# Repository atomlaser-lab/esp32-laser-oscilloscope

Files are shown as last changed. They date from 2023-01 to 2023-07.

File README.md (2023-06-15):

# ESP32 Remote Oscilloscope + MOGLabs DLC control

This project is a remote browser-based oscilloscope and controller intended for monitoring, toggling and adjusting the frequency lock on a MOGLabs Diode Laser Controller (DLC). An ESP32 development board interfaces with the DLC and hosts a dashboard webpage.

This README contains [Instructions](#instructions) for setting up and using the project as well as useful [Background information](#background). A list of [bugs and suggested improvements](#bugs-and-improvements) is at the end. The project was developed and tested using the PlatformIO Extension in VSCode, with a model 502 DLC. It requires an ESP32-DevkitC development board (see [specs, board comparison & resources](https://www.espressif.com/en/products/devkits/esp32-devkitc)), and should work with either WROVER or WROOM versions. It was tested with the ESP32-DevKitCVE V4 board, which has a WROVER module.

## License
[GPLv3](LICENSE)

## Repository structure
Branches: currently just `esp`. Branches for other microcontrollers might be useful in future.

PlatformIO:
- `src/main.cpp`: ESP32 code.
- `data/`: files stored on the ESP32 flash memory. Contains the webpage + `config.json`.
- `platformio.ini`: PlatformIO project config.

Hardware:
- `board-design/`: TODO
- `enclosure/`: FreeCAD files for the 3D-printable housing.

Other:
- `.vscode`: recommended extensions
- `assets/`: images for this README.

## Instructions
[Software config](#program-configuration-and-upload) - [Hardware](#hardware-connections-and-settings) - [Browser interface](#interface)

### Program configuration and upload
This section assumes you are using the PlatformIO extension in VSCode.

Specify project options by editing `config.json` (in `/data`). If connecting to an existing WiFi network (the default option), you must specify its `ssid` (network name) and `password`. If instead `host` is set to `true`, the ESP will host its own network (intended for testing purposes) with credentials `host_ssid` and `host_password`. `host_password` must contain at least 8 characters; otherwise hosting will fail. Note that the ESP32 only supports 2.4GHz WiFi (not 5G).

Other parameters are optional, with defaults and descriptions as shown below in **Example 2**.

**Example 1: minimal WiFi connection**
```
{
  "ssid": "MyWiFiNetwork",
  "password": "verysecurepassword",
}
```

**Example 2: all options**
```
{
  "name": "TestName",
  "host": false,
  "ssid": "MyWiFiNetwork",
  "password": "verysecurepassword",
  "host_ssid": "ESP32_Laser_Lock",
  "host_password": "laserlock",
  "host_channel": 1,
  "default_duration": 60,
  "default_resolution": 2,
  "default_ip": "192.168.1.1"
}
```

| Parameter | Description |
| --- | --- |
| `name` | Display name for the device |
| `host_channel` | If hosting, the WiFi channel used. |
| `default_duration` | Default length of a measurement packet (millisec), adopted on board startup. |
| `default_resolution` | Default time (ms) between consecutive samples in a measurement packet, adopted on startup. |
| `default_ip` | If available, the local IP address the ESP32 will adopt. Applies to both hosted and external networks. |

To **upload the project to the board**:
1. Connect the board to your computer via a cable.
2. Upload the filesystem to the board:
    - '*Build filesystem Image*' (in PlatformIO menu)
    - **Ensure all serial monitor connections with the board are closed**. PlatformIO does not do this automatically when uploading the filesystem (though it *does* when uploading the code in step 4)
    - '*Upload filesystem Image*' (in same menu)
3. '*Build*' (PlatformIO menu, or tick symbol in status bar)
4. '*Upload*' (PlatformIO menu, or rightwards arrow in status bar)

The program will restart each time the ESP is plugged in, code/filesystem is re-uploaded, or the RST button is pressed.

Open the serial monitor to see the board's local IP. You may need to reset the program (RST button) while the monitor is open for the message to display. If `default_ip` is specified (and was successfully adopted), you can skip this step.

Connecting to the board's IP in a browser (e.g. `http://192.168.1.1`) while on the same network will open the [Interface](#interface).

### Hardware
This section assumes you already have a laser-locking setup using the MOGLabs DLC. For information about laser locking and the DLC, see [Background](#background).

#### Overview
The MOGLabs DLC contains fast, robust analog control circuitry for locking the laser frequency. The point of this project is to allow the lock to be acquired via microcontroller control of the DLC, while leaving the DLC to handle the actual locking process.

The project currently has three inputs and three outputs. The photodiode , error and trigger (digital) signals from the DLC are input to the board and transmitted to the remote user interface. The board outputs two digital (TTL) control signals to enable/disable the FAST and SLOW lock, and an analogue signal (via external DAC) to adjust the laser's frequency offset. More detailed reasoning behind the electronic design is explained in [Hardware design](#hardware-design).

The next section contains some guidance for putting together the PCB. The ESP32 board can be soldered to the PCB directly for the smallest possible footprint, but it is much more flexible to attach it via additional male and female headers. The external frequency offset voltages used in this project also require soldering an additional resistor into the DLC (see [Connecting to the Diode Laser Controller](#connecting-to-the-diode-laser-controller)). 

Part numbers and quantities for **two** PCBs are specified in `board-design/moglabs-remote-locking-board.txt` for the DigiKey electronics distributor, which can be imported directly into a DigiKey cart. This list is missing capacitors C6 and C7 (see table below). Auxiliary parts (headers + DLC resistor) are similarly specified in `board-design/auxiliary-parts.txt`. An optional 3D-printable housing for the project can be found under `enclosure/`. 

Electronic design was done in KiCAD 6, and the (optional) enclosure was generated with FreeCAD 0.20.2.

#### Printed Circuit Board
Relevant files are in `/board-design`. Gerber files for manufacturing the PCB can be found in `generated.zip`, and PCB circuit and layout schematics (`.pdf`) are under `plots/`.

```
board-design/
|-- generated.zip
|-- plots/
  |-- moglabs-remote-locking-board.pdf
  |-- moglabs-remote-locking-board.pcb
|-- moglabs-remote-locking-board.txt
|-- auxiliary-parts.txt
|-- ...
```

This section briefly describes the circuit, shown below. For more details, see `board-design/README.md`.

Left: input for the error signal ('Lock'), photodiode signal ('PD') and trigger. A 1.5V offset is added to the (bipolar) error signal to make it positive, and both Lock and PD voltages are clipped to remain within the board's 0-3.3V pin range. The DLC trigger is +5V, which is divided down accordingly.

Bottom left: power regulator to introduce +5V and -5V VDD and VSS rails from the board's 5V power pin.

Right: analog frequency-offset output signal (J6) controlled by an external DAC (U4) and dual opamp (U3). The DAC output is divided down considerably, as a 1V adjustment to PZT MOD corresponds with about a third of the piezo's (i.e. frequency) range. A variable resistor gives additional control over the output voltage range (this will need to be tuned to observe an output signal).

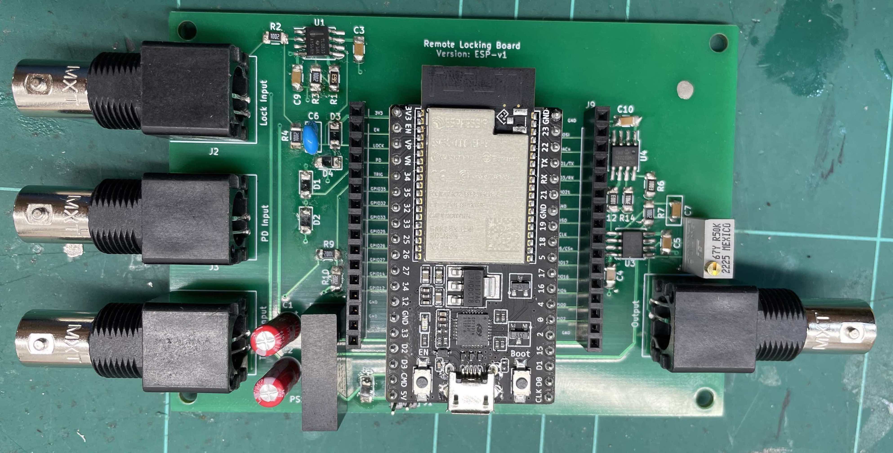
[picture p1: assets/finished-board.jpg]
Soldered board


The required parts for **one** PCB are in the tabe below. For specific part numbers, see the DigiKey text files specified above. Note that the capacitor numbering in the schamatic skips C8.

Terminology:
- 8-SOIC is a component shell size/type (comonly opamps, dacs)
- DAC: digital-to-analogue converter
- SPI: Serial Peripheral Interface
- SMD: Surface-mounted device
- 1206: component size

| Requirement / Part description | PCB Locations | Total Qty | Notes |
| --- | --- | --- | --- |
| IC 8SOIC 12-Bit single-output DAC with SPI and internal voltage reference (2.048V/4.096V) | U4 | 1 | code assumes [MCP4821](https://www.microchip.com/en-us/product/MCP4821) |
| IC 8SOIC JFET opamp 1-circuit | U1 | 1 | |
| IC dual (2-circuit) opamp GP 8SOIC | U3 | 1 | |
| ESP32 DevKitC VE (WROVER/WROOM) | U2 | 1 | |
| 16-position 2.54mm female row header | J5, J9 | 2 | |
| 2-pos 2.54mm male header | J1 | 1 | |
| 50 kΩ potentiometer 0.5W | RV1 | 1 | |
| DC DC converter dual 5V 1W | PS1 | 1 | |
| BNC socket | J2, J3, J4, J6 | 4 | |
| 40V 1A Schottky diode (SMD 1206) | D1,D2,D3,D4,D5 | 5 | |
| 100 nanofarad 50V ceramic capacitor (SMD 1206) | C3, C4, C5, C9, C10 | 5 | |
| Polarised through-hole capacitor 4.7 uF 25V | C1, C2 | 2 | |
| 10 nF through-hole capacitor | C6 | 1 | Not on DigiKey list |
| 100 nF through-hole capacitor | C7 | 1 | Not on DigiKey list |
| 10 kΩ 0.5W resistor (SMD 1206) | R2, R3, R4, R7, R9 | 5 | |
| 20 kΩ 0.5W resistor (SMD 1206) | R10 | 1 | |
| 100 kΩ 0.5W resistor (SMD 1206) | R6, R12 | 2 | |
| 3.9 kΩ 0.25W (SMD 1206) | R14 | 1 | |
| 56 kΩ 0.25W resistor (SMD 1206) | R1 | 1 | |

Optional headers for mounting the ESP32 devkit on the PCB:

| Description | PCB Locations | Total Qty | Notes |
| --- | --- | --- | --- |
| 19-position 2.54mm female header | J7 & J8 (not marked) | 2 |  |
| 19-position male header for ESP32 | On ESP32 | 2 | Likely included with ESP32 devkit |

#### Tests
- TODO

#### Connecting to the Diode laser controller
Take care when connecting to the DLC, particularly to avoid shorting the digital control pins. Ensure the internal DIP switch settings of the DLC are set appropriately (e.g. as in [Moglabs Diode Laser Controller](#moglabs-diode-laser-controller)). For reference, at the end of this section are the DLC panels (from the [DLC manual](https://www.moglabs.com/products/laser-electronics/diode-laser-controller)) and the location of the HD12 header.

##### **POWER**
The board can be powered via the micro-USB connector (5-12V) or the PCB's J1 two-pin header (5V).

The DLC has an IEC output (rear panel, second from the left), which is a direct connection to the DLC's input power (after the mains filter) and can be used to power the ESP32 using an IEC cable and 12V power adapter. This is convenient and ensures the ESP32 shares the same ground as the DLC.

Safe input voltages for the board's pins are 0-3.3V, and is it **not** tolerant of voltages outside this range. Be careful to keep the DLC and ESP32 ground voltages compatible.

##### **SLOW and FAST**
Digital control of the DLC is via the internal HD12 header, which is located as shown below. **Do not** confuse it with the similar-looking header nearby. The ESP's digital pin voltages are compatible with the HD12 header and can be connected directly as per the table below.

| Board pin | HD12 pin(s) |
| --- | --- |
| GPIO14 | 3 |
| GPIO4 | 5 |
| GND | 4, 6 |

Ensure that the sweep range is set appropriately, and that the front-panel LOCK and FAST switches are **off** so that these can be enabled remotely.

##### **TRIGGER**
The MOGLabs DLC trigger signal output (TRIG on rear panel) fires a +5V rising edge (i.e. 0V to 5V) at the trigger point of the sweep, i.e. the *centre* if using the DLC's default (internal) sweep. This can be safely connected to the appropriate BNC input on the PCB.

##### **INPUT SIGNALS**
Set the CHAN A and CHAN B selector dials to (photodiode) Input and (feedback) Error respectively; note that both channels can output the photodiode, but only CHANNEL B can output the error signal. Connect these to their respective PCB inputs.

The photodiode input offset and error signal offset can be adjusted respectively using the INPUT and ERROR OFFSET dials on the DLC's front panel. The photodiode should be in the range 0-3.3V, and the error centred for locking (i.e. about zero).

##### **FREQUENCY CONTROL**
Test the frequency control output (J6) before connecting, to ensure it is within the range +/- 0.2V. Before connecting, a 5kΩ resistor must be added at location R113 on the DLC's circuit board to allow adding an external frequency voltage offset.

| Description | **DLC** location | Total Qty |
| --- | --- | --- | --- |
| 5kΩ size 0603 SMD resistor  | R113 | 1 |

Once this is added, connect J6 via BNC to the DLC's SWEEP/PZT MOD input.

##### Reference images

**Location of HD12 Header**
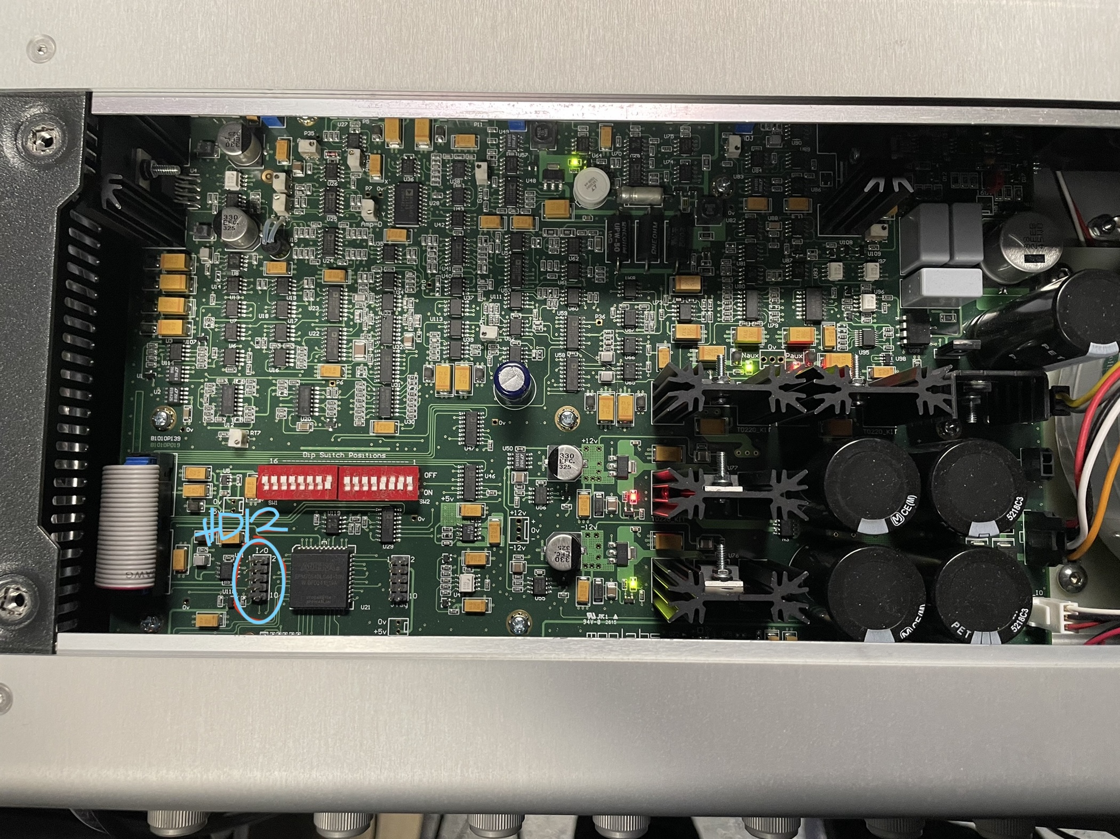
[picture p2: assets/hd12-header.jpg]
HD12 header location


**Front DLC panel**
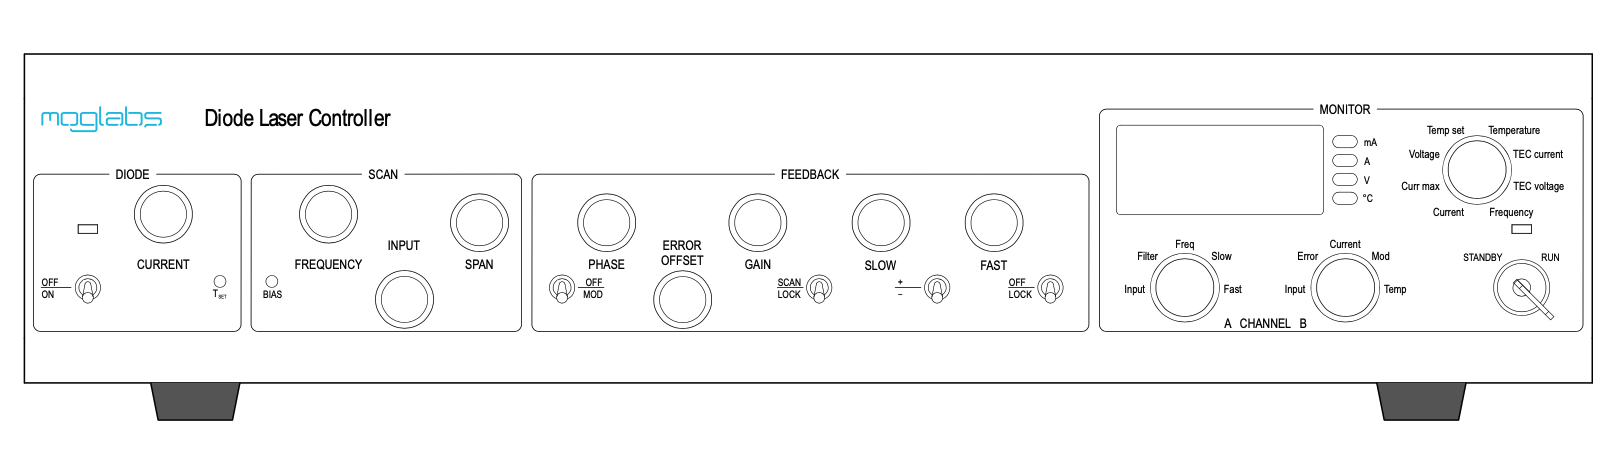
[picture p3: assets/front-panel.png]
DLC502 front panel


**Rear DLC panel**
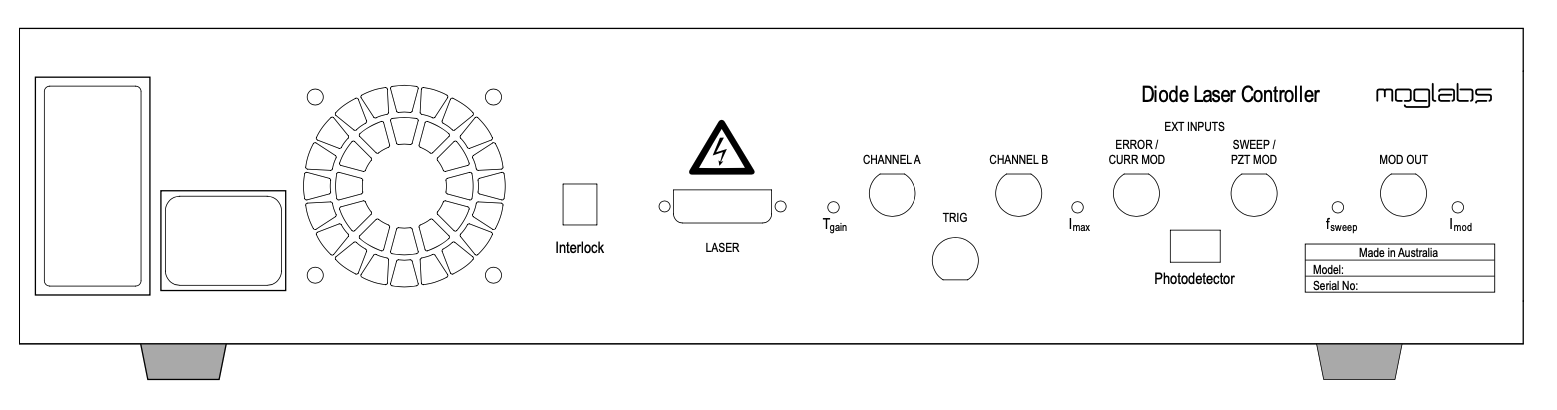
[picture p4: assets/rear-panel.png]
DLC502 rear panel


### Interface
Connecting to the board's IP in a browser should display the page below. If you didn't set the IP in `config.json`, you can list the devices on the local network using `arp -a` in a terminal, or check the IP by restarting the ESP32 while connected to the serial monitor.

Only one user is allowed to connect at a time, to prevent conflicting commands.

Controls for the DLC, the ESP32, and the browser display are split into three separate panels.

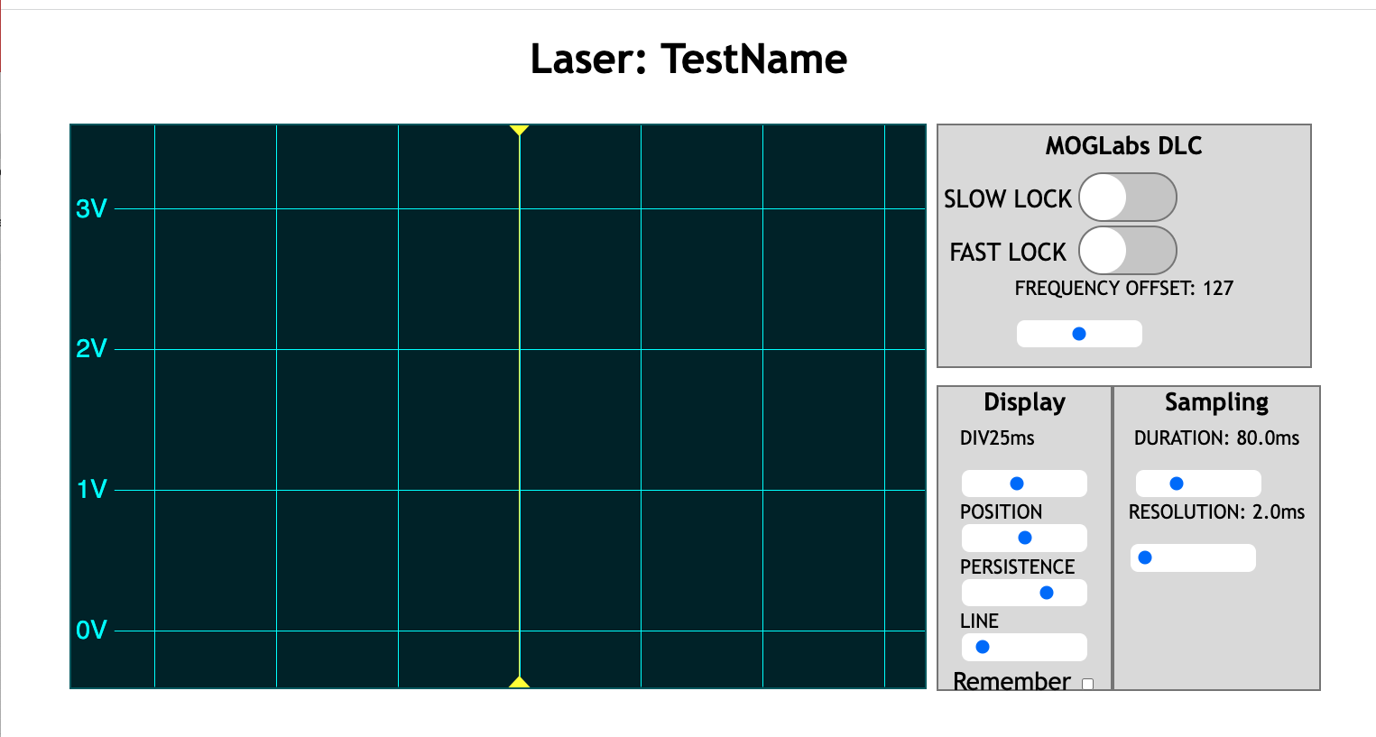
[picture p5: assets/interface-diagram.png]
Interface diagram


#### DLC Control
The top panel has switches for toggling the SLOW and FAST lock. These switches are subject to a cooldown, and will also only change appearance once the ESP has confirmed the command was successful.

The 'Frequency Offset' slider controls the external voltage to the piezo. The displayed number is arbitrary.

#### Sampling settings
Signal measurements are sent from the board to the browser in groups. The RESOLUTION and DURATION sliders respectively control the time between individual measurements and the size of each group sent to the browser.

#### Display settings
These affect how the signal is displayed in the browser. Check 'Remember' to remember these settings.

| Slider| Function |
| --- | --- |
| DIV | Time period represented by each horizontal interval on the display. (i.e. horizontal scaling) |
| POSITION | Horizontal position of the trigger point in the signal, marked by the yellow indicator. |
| PERSISTENCE | How quickly previous trigger signals fade from the screen. |
| LINE | The line thickness. |

## Background
This section explains useful background on laser operation and the MOGLabs DLC, as well as summarising relevant details about the ESP32 and giving an overview of how the program works.

### Lasers (motivation and operation)
In various applications we would like to 'lock' the frequency of a laser to a specific atomic transition frequency, either because these are physically constant and known to high precision or because we are working with that particular transition.

The output power and frequency of an external-cavity diode laser (ECDL) (TODO: useful reference here) are controlled primarily (though to differing extents) by three factors:

1. Current injected to the diode
2. Temperature
3. Cavity length (controlled by piezo voltage).

An ECDL internally permits light to (co)exist at a discrete set of frequencies ('modes') determined by the length of the cavity. This light bounces back and forth through a 'gain medium', which repeatedly amplifies it (up to the limit of power provided by the injection current). On each trip, a small amount exits the cavity. The diagram below is an example of frequency-dependent gain (black) affecting different modes (red) (image credit: [this stackexchange answer](https://physics.stackexchange.com/questions/355223/laser-gain-curve) under the [CC BY-SA 4.0 license](https://creativecommons.org/licenses/by-sa/4.0/)).

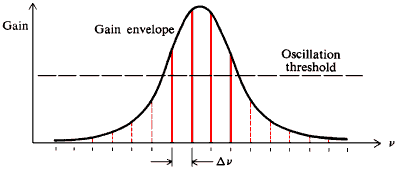
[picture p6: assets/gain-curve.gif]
Gain curve diagram


At a given temperature and injection current, the gain medium amplifies different frequencies by different amounts, known as a gain curve. When 'lasing' (i.e. sufficiently high current), the most strongly-amplified of the allowed modes will quickly dominate, producing a single-frequency output (provided this amplification is enough to overcome losses).

Even with constant current, temperature and cavity length, the laser frequency tends to drift, which is mitigated using feedback. However, if two modes have similar amplification, the dominant one can switch erratically ('mode hopping') with a corresponding distinct jump in frequency. These jumps typically can't be remedied by feedback, requiring the laser to be re-locked. The aim of this project is to allow this re-locking to be performed remotely.

### Frequency locking (Saturated absorption spectroscopy)
To produce an error signal, we make use of the fact that an atom will only absorb light that is near a transition, roughly within a linewidth (i.e. ~inversely proportional to the lifetime of the corresponding state). Linewidths vary between kHz and GHz.

[ TODO: diagram of vapour cell with counterpropagating beams ]

Suppose a laser passes through a gas. The *apparent* frequency of the laser depends on the velocity of an atom (the Doppler effect). Since the atoms have a range of velocities, the laser will be absorbed in rough proportion to the number of atoms at the corresponding velocity, so the range of absorbed frequencies is 'Doppler-broadened' and the output intensity varies on the order of GHz.

If we reflect the laser back through the cell, it will now excite (i.e. be absorbed by) atoms of the *opposite* velocity, reducing the intensity again. This will not occur, however, if these atoms were *already* excited by the forward beam, i.e. if the beam is exactly on resonance with the zero-velocty atoms. So, we get a small dip in absorption when at the transition frequency.

[ TODO: diagram of doppler-broadened peak and saturation dip]

[ TODO: diagram of Rb85 absorption spectrum and error signal, e.g. DLC manual Fig. 1.3]

We can use the absorption dip as a reference point via either *AC* or *DC* locking. In both cases, we first produce an *error signal* whose voltage indicates the sign and size of any frequency drift, being zero at the reference point. Any error is then corrected via a feedback signal to the laser.

DC locking uses the absorption signal itself (as measured by the photodiode) as the error signal, by applying a voltage offset so that the signal passes zero on the side of the absorption peak. However, this easily becomes unlocked as the laser power drifts relative to the reference voltage.

AC is more reliable and allows you to lock exactly to the peak of a signal. This is done by rapidly shifting the signal from side to side, by deliberately modulating (dithering, i.e. rapidly oscillating) either the laser frequency (via the injection current) or the atomic resonance frequency (via a magnetic field). The MOGLabs DLC supports both methods, but in this case we used the former. Passing the modulated signal through a lock-in amplifier yields the derivative of the absorption spectrum, which passes through zero at the centre of the peak and hence serves as an error signal.

### MOGLabs Diode Laser Controller
This section is a reference for how the DLC works, convering information relevant to the design and understanding of the project. It summarises parts of the MOGLabs DLC manual (description and manual [here](https://www.moglabs.com/products/laser-electronics/diode-laser-controller)) and my own experience. The DLC's settings are mostly controlled via internal DIP switches (small, manual switches). Below is a reference; selections used in this project are in bold, and a brief explanation is on the right. The rest of this section will hopefully make clear what these DIPs do. 

| DIP Switch | Off | On | Relevance |
| --- | --- | --- | --- |
|1 | **DISC fixed** | DISC ON| Our laser doesn't have DISC |
|2 |STACK fixed| **STACK ON**| Enables control of the piezo |
|3 |Current dither OFF| **Current dither ON** | Enables *laser current* modulation when OFF/MOD is enabled |
|4 |Current bias OFF| **Current bias ON**| Enables BIAS, to avoid mode hopping|
|5 |**Internal error**| External error| We use the DLC's generated error signal
|6 |**External current mod OFF**| External current mod ON| Leave the DLC to do its thing
|7 |**AC lock**| DC lock| AC locking is more reliable
|8 |**Single photodiode**| Dual photodiode| Measuring direct intensity or the difference of two intensities, using the MOGLabs photodiode.
|9 |**Sweep internal**| Sweep external| Internal sweep works well, and SWEEP/PZT mod is needed for electronically adjusting the frequency offset
|10| STACK feedback –| STACK feedback +| Depends on your setup
|11| STACK sweep +| STACK sweep –| Depends on your setup
|12| **AC current feedback** | DC current feedback| FAST feedback should usually be AC no matter what
|13| **STACK internal**| STACK external| We want the DLC to control STACK, not us.
|14| DISC internal| DISC external| Irrelevant if no DISC.
|15| Default| External slow error| See manual
| 16 | See manual.

The DLC controls all three of the ECDL's piezo voltage (cavity length), temperature and injection current. The voltage applied to the piezo is known as the STACK (some lasers have a second piezo, *DISC*, which can also be controlled - I ignore that here.). At any given time, the DLC is either SCANning or LOCKing the laser frequency.

The voltage supplied to STACK ranges from 0-120V. When scanning, this voltage is adjusted according to the DLC's *sweep signal*, which has a range of 0-2.5V. The width of the scan (corresponding with full 0-2.5V range) is controlled by the SPAN dial and cannot be controlled externally. The DLC's trigger fires when the sweep signal crosses 1.25V; when locking is activated, the laser is first moved to this point before locking to the nearest zero-crossing of the error signal. Offsets to the input signal and error signal are adjusted using the INPUT OFFSET and ERROR OFFSET dials, respectively.

The DLC can either generate its own internal sweep signal, or use an *external* signal input to SWEEP/PZT MOD. The direction (polarity) of the internal sweep can be chosen using DIP switch 11, and its frequency can be varied between 4Hz-70Hz using the *fsweep* front panel trimpot. Diagrams of the internal sweep and corresponding trigger output are provided in the manual (Fig. 1.2). The sweep sawtooth is illustrative only; the DLC doesn't produce a sawtooth with perfectly vertical edges - they actually have a slight slope, to prevent the piezo from snapping back into place too forcefully (which creates a rattling sound). If this still happens, you may need to reduce the sweep frequency (fsweep trimpot) or SPAN.

The piezo offset (i.e. laser frequency) at the lock point is determined by the FREQUENCY dial. In particular, it is *not* affected by the use of an external sweep signal, which is only useful for controlling the speed, shape and (potentially asymmetric) width of the frequency path up to the maximum width set by SPAN. To limit mode-hopping while scanning, the diode current can be 'biased' to adjust itself linearly with the sweep voltage; this is enabled using DIP switch 4, with the direction and extent of adjustment controlled by the BIAS front trimpot.

#### Locking
The DLC provides feedback to the laser via:

1. The (relatively SLOW) piezo - for larger, slower drifts
2. The (comparably FAST) injection current - for small, rapid frequency fluctuations.

Each feedback is enabled by the corresponding switch (or digital control), and the direction can be reversed using DIP switch 10. The choice of AC or DC locking is controlled by DIP 7. The DLC provides an optional 250kHz modulation (switch OFF/MOD on front panel), either as an output (for e.g. dithering the atomic resonance) or directly to the laser current (see DIP switches); this is intended to aid AC locking. In either case, the amplification of the error, slow feedback and fast feedback can each be adjusted from 0-40dB via the GAIN, SLOW and FAST dials respectively. In the AC case, the phase of the lock-in amplifier (PHASE) may also need adjusting. Phase can be used to switch the sign of the SLOW feedback; to switch the sign of the FAST feedback, use the +/- switch. Note that the the MOGLabs photodetector outputs 30mV/microWatt.

Depending on which DIP switches are active, the SWEEP/PZT MOD input (rear panel) allows replacement of either the sweep signal (DIP 9), error signal (DIP 15) or direct piezo control voltage ('STACK') (DIP 13) with an external signal. However, the **only option** to externally adjust the lock frequency while making use of the DLC's (fast, robust, analogue) inbuilt control circuitry is to instead add a resistor (~5kΩ, size 0603) at location R113 (see the DLC manual), while leaving the aforementioned DIP switches OFF. This *adds* the SWEEP/PZT MOD input voltage to the existing laser piezo signal (STACK) under all circumstances (after a 48x scaleup).

Digital control of the DLC is via its internal HD12 control header, with the following pins:

| Pin | Signal |
| --- | --- |
|1 | Laser ON (low: off) |
|3 | Slow Lock (low: sweep) |
| 5 | Fast Lock |
| 7 | Hold |
| 9 | +5V |

Pins 2,4,6,8,10 are ground. 

These control pins are OR-ed with the front panel switches, so digital locking control only applies if the SCAN/LOCK switch is set to SCAN, and (for fast lock) the OFF/LOCK switch to OFF.

### ESP32
The ESP32 is a system-on-chip (SoC) with built-in WiFi, with input-output access via a *module*. For ease of use, this is often mounted on a *development board*, which provides easy pin access and various other useful components (e.g. ADC, voltage regulation). The same board 'form factor' (shape and pin arrangement) can be paired with different module versions; this project requires a ESP32-DevKitCVE V4 board, either with the ESP32-WROOM or ESP32-WROVER module.

An excellent introduction to the ESP32 can be found at [Last Minute Engineers (LME)](https://lastminuteengineers.com/getting-started-with-esp32/). This includes tutorials on ESP web servers and GPIO interrupts, both of which are used in this project. However, their tutorial uses (1) an older and slightly different board and (2) the Arduino IDE, while this project was developed using the PlatformIO IDE for VSCode (including the instructions in this README). 

An excellent video tutorial for PlatformIO+VSCode can be found [here](https://www.youtube.com/watch?v=JmvMvIphMnY). The project's source code uses the ESP32 Arduino framework ([documentation here](https://espressif-docs.readthedocs-hosted.com/projects/arduino-esp32/en/latest/index.html)). 

For the DevKitC-V4, a look at the [Getting Started Guide](https://docs.espressif.com/projects/esp-idf/en/v4.4.5/esp32/hw-reference/esp32/get-started-devkitc.html). Detailed specs can be found in the [official ESP32 datasheet](https://www.espressif.com/sites/default/files/documentation/esp32_datasheet_en.pdf). Below is the pin reference from the Getting Started Guide (note GPIO stands for General Purpose Input Output):

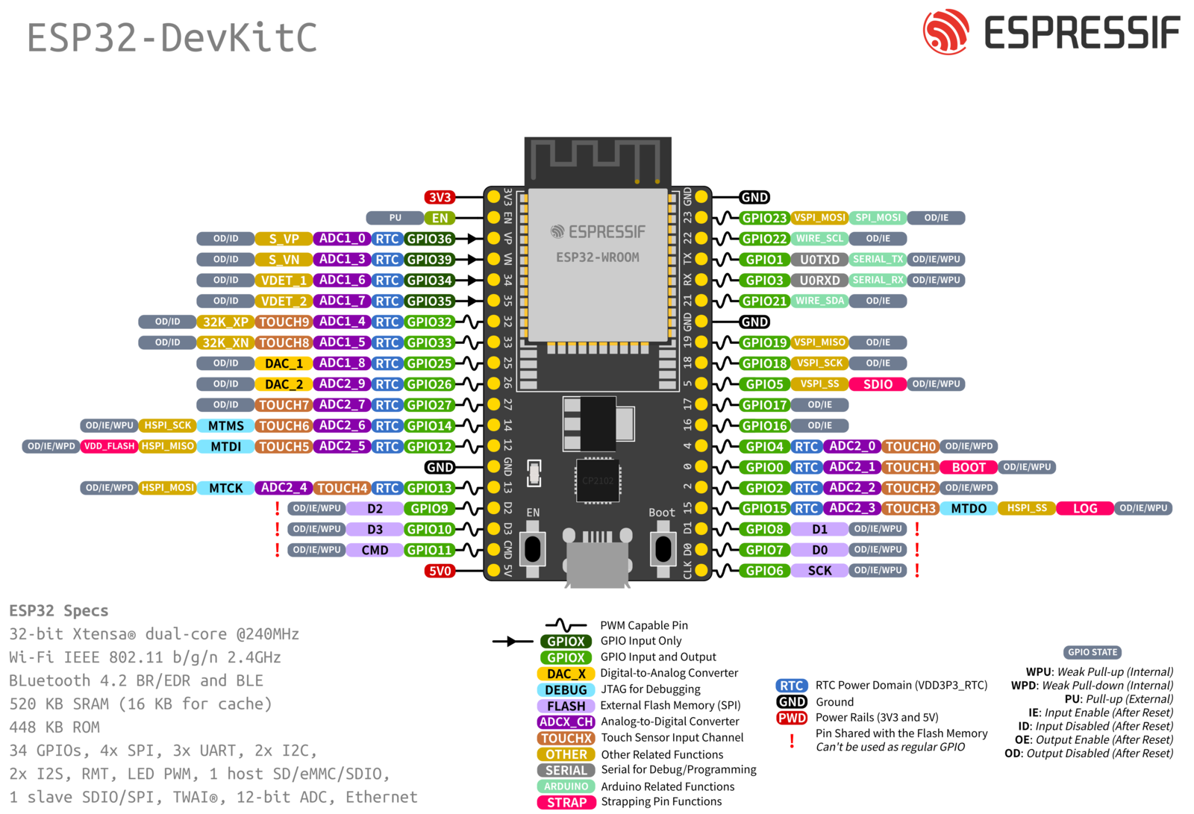
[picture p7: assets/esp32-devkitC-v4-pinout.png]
ESP32 pin reference


Note that not all pins are safe to use; this is discussed more in [Hardware design](#hardware-design).

The ESP32 has two 12-bit analog-to-digital converters (ADCs), which together can read analogue inputs from fifteen pins; however, ADC2 cannot be used while WiFi is in use, and so the analog input pins for this project have been chosen from those available to ADC1. Note that this issue prevents use of the (similar but less powerful) ESP8266 for this project, as it has only one ADC (which is WiFi-blocked).

ESP32 also has [a digital-to-analog converter](https://docs.espressif.com/projects/esp-idf/en/latest/esp32/api-reference/peripherals/dac.html) (DAC); however, this was not sufficient for this project.

The ESP32 only operates on 2.4GHz WiFi band (not 5.8GHz). The longevity commitment for the original ESP32 module is until [Jan 1, 2028](https://www.espressif.com/en/products/longevity-commitment)

### Hardware design
This section explains some details affecting the electronic design of the PCB.

The pins on the ESP32-DevKitC-V4 are (officially) only tolerant of 0-3.3V voltages, requiring appropriate input clipping for protection. The DLC's trigger is a 0-5V square signal, 

The previous section noted that only one of the ESP32's two ADCs can be used concurrently with WiFi. More importantly, WiFi use causes periodic spikes in power draw, which adds enough noise to the DAC output to prevent successful laser locking. Neither the board's inbuilt power regulator, nor additional bypass capacitors on the frequency-control output signal, are enough to avoid the issue. Therefore, we use an external MCP4821 DAC controlled via Serial Peripheral Interface (SPI). This also has a 12-bit resolution, higher than the inbuilt 8-bit DAC. The impedance of the SWEEP/PZT MOD input on the DLC is 5kΩ.

#### Pin choice
Can't use TX & RX pins, as they're used when flashing the board (even via USB). Pins which affect boot mode (0, 2, 12, 15) have been left alone. WROVER reserves GPIO 16/17 for internal use (controlling the SPI PSRAM). Inbuilt DAC (GPIO25/26) and the remaining ADC1 pins (GPIO33,32,35) have also been left available.

See Last Minute Engineers and [the boot mode docs](https://docs.espressif.com/projects/esptool/en/latest/esp32/advanced-topics/boot-mode-selection.html).

#### External DAC

This project uses the MCP4821 DAC to produce the frequency-adjustment signal, controlled from the ESP32 via serial peripheral interface (SPI).

The ESP32 has two SPI buses available for general use: SPI2 (HSPI) and SPI3 (VSPI). 'H' and 'V' don't signify anything. Any pins can be set as the corresponding interface pins; the defaults are indicated in the pinout diagram, but in this project non-default pins are used.

SPI communication with the MCP4821 is explained in its datasheet. Briefly: chip-select is driven LOW to initiate each data transfer, then 16 bits are transferred: four config bits followed by 12 value bits. The value bits are stored in the DAC's input register, and transferred to the output (Vout) when LDACn is pulled low. The current software keeps LDACn permanently low, so that the input value is transferred immediately to output.

### Software design
This section gives a general overview as well as some relevant details of the code. Many more comments are scattered throughout the source.

On startup, the ESP32 reads from `config.json`, sets up WiFi as a host or station accordingly, and begins a webserver (run asynchronously in the background) to serve the static webpage interface. Only one user is allowed to connect at a time, to prevent conflicting commands.

Since the MOGLabs DLC fires its trigger in the *middle* of each sweep, the simplest way to capture the entire sweep is to continually measure the input signals. The signal is sampled in 'packets', with a certain interval between each sample (~0.1-10ms), and a specified packet duration (~30ms-1s) before it is sent to the web client and a new packet begun. For simplicity, each 12-bit ADC measurement is reduced to a single byte (8-bit). Triggers fire an interrupt which records the time of the trigger in microseconds. When a packet is complete, a 'herald' message (JSON text) is sent over the websocket, containing the packet's start and end time (microseconds) as well as the trigger time (if any). The measurements themselves are then sent on the websocket as a binary buffer (note that websocket messages are always reconstructd in-order by the client).

On the web client, received packets are stored and displayed according to the most recent trigger, with packets from previous triggers faded (but still visible). This was originally designed to allow gaps between measurement packets to be filled by previous packets, though there is no longer a significant gap. Old data is culled from time to time.

Messages sent from client to the board to control the laser frequency offset are sent as two-byte integers over the websocket. Commands for toggling the lock and updating the measurement interval/duration are sent via HTTP. The interface waits until it receives confirmation of success from the ESP before updating the SLOW/FAST switches. Messages are sent periodically (every 10s) to check the control-state of the DLC; this is also done when toggling the lock.

`cpp` source code: in the Arduino framework, the pin number is the GPIO number (at least in PlatformIO).

## Bugs and improvements

### Known bugs
- (Serial monitor) `ERROR: Too many messages queued`. The ESP32 has a message queue limit of 16 and any others will just be discarded. When the sampling duration is small it is unable to flush the queue frequently enough.
- (Serial monitor) `open(): /littlefs/file does not exist`
  - this is a meaningless error, and to get rid of it you have to modify `ESPAsyncWebServer/src/WebHandlers.cpp` 
  - See https://github.com/lorol/LITTLEFS/issues/2

### TODO
- Save HD12 & DAC settings on reset
  - Allow config file to be modified remotely?
- DLC-safe reset procedure
- Look into uploading the config file Over-The-Air.
- Vertical DIV scaling on display, independently for photodiode and error signals.
- "Invert signal" button
- Reset sample-settings sliders to their previous value if HTTP POST message fails.

### Suggested improvements
- Mobile-friendly webpage (cf. `@media-query`)
- Optional user authentication
- Automatic mode-hop detection and re-locking
- Higher monitoring resolution? (Currently 8-bit, but ESP32 ADCs are 12-bit)
- Input modes: continuous, on-request, single trigger
- Highlight clipped sections of the signal in red
- Button to remotely restart the ESP32 and/or restore default measurement settings.
- Cookies for display settings don't seem to be respected when the board restarts.
- Interface information
  - Warnings/errors from the ESP
  - Websocket connection status
  - Actual measurement resolution of most recent packet
- README
  - Serial monitor error message reference for custom errors

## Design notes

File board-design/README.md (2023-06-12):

# Circuit and PCB for remote locking

This PCB and associated enclosure is intended to be used in conjunction with an ESP32 development board for the purposes of providing a remote interface for locking MOGLabs diode lasers.  It is intended that the MOGLabs DLC handles the locking process, and that this board and its circuitry is used for acquiring the lock.  The PCB provides a convenient way of acquiring input signals and producing an appropriate output signal for the DLC.

PDFs of the circuit diagram and the PCB can be found under the plots/ directory.  Electronic design was done in KiCAD 6, and the enclosure was generated with FreeCAD 0.20.2.  Gerber files for manufacturing the PCB can be found in "generated.zip".  Digikey part numbers and quantities for 2 boards can be found under 'moglabs-remote-locking-board.txt' and 'auxliliary-parts.txt'.

## Circuit design

The idea behind this project is to use a WiFi-enabled microcontroller to measure locking signals from a diode laser, present those to a user through a web interface, accept user input to enable the lock or change the lock position, and then to produce output signals to act on user input.  The core of the board is an ESP32-DevKitC-v4 board, which can use a number of different microcontrollers but with the same board pinout and form factor.  The part chosen for this project is the ESP32-DEVKITC-VE with an ESP32-WROVER-E microcontroller.  Other chips with the same pinout and form factor can also be used.

Two analog signals are recorded by the microcontroller unit (MCU): the error or locking signal, denoted as "Lock", and the raw photodiode signal, denote as "PD".  The MCU's ADCs can only record positive voltages, and the error signal by definition must be bipolar, so an op-amp and associated components is used to add a 1.5 V offset to the signal while also inverting it (the inversion is simply a side-effect).  This should put the error signal at the midpoint of the ADC's voltage range.  A pair of Schottky diodes is used to clip the voltage to the 0 V and 3.3 V rails.  The PD signal should always be positive, and it is similarly clipped to the 0 V and 3.3 V rails.  The Lock signal is recorded using ADC1_CH0 or GPIO36, and the PD signal is recorded using ADC1_CH3 or GPIO39.  Finally, the trigger generated by the MOGLabs DLC is recorded using the digital input channel GPIO34 after passing through a voltage divider to bring the 5 V level to 3.3 V.  As the actual lock is handled by the DLC the quality of the recorded input signals is not particularly important, and we have thus used the MCU's internal ADCs.

The output analog signal is more important, and the on-board DACs don't work well when the WiFi is also running.  Therefore, we use a 12-bit DAC (MCP4821) which interfaces with the MCU via SPI to produce the output signal for the external piezo control.  The DAC produces a unipolar output, so one channel of a dual-channel op-amp is used to offset the voltage and generate a bipolar output.  The DAC in this case has a selectable voltage reference, and here we have assumed that it is set such that the reference voltage is 4.096 V which is also the default on power-on.  Resistors R6, R7, R12, and R14 are chosen to produce voltage outputs as close as possible to a bipolar output.  The resistors are chosen to give an approximate +/-0.2 V output range.  The second op-amp is combined with a trimmer potentiometer to give more control over the output voltage range.  Both amplifiers operate in an inverting configuration, which gives a net non-inverting output.

It is expected that power will typically be supplied via the development board's USB connector, which is nominally +5 V.  However, users can instead supply +5 V to the J1 pin header, which will power both the development board and the rest of the circuitry.  Bipolar +/-5 V is generated by the switched-mode power supply PS1, and the VDD and VSS pins on the op-amps are connected to the appropriate pins on the power supply.  This power supply can supply up to 100 mA, and it technically has a minimum load of 10 mA, but the datasheet states that no damage will occur if operated with loads below 10 mA.  It is expected that output ripple will probably be worse than specified if the current draw is less than 10 mA.  If a bipolar supply is present, one could not populate PS1 and instead connect the bipolar +/-5 V rails to the appropriately labelled connections on the board, possible through the use of a standard 2.54 mm pitch pin header.  Users would then need to connect the +5 V rail to the development board.

The development board can be connected to the PCB in one of two ways.  The first is to solder male pin headers to the PCB and then solder the development board to the male pin header: this will provide the smallest possible footprint.  The second way is to solder female pin sockets to the PCB and then solder male pin headers to the development board and attach it to the PCB in a solder-less connection.  This is probably the better option, even though it involves more soldering, because if the development board needs to be removed it is a hassle to de-solder 38 separate pins.

Finally, most of the GPIO pins on the development board are broken out on the female pin sockets J5 and J9.  When programming, the user can choose appropriate GPIO pins for driving the DLC digital control pins.  It is recommended that wires connected to male pin headers are used for the connection.

The PCB has four M3 mounting holes in the corner of the board.  These can be safely used with standard metal bolts as they are not connected to any of the electrical signals.

## Enclosure

The enclosure is designed with the expectation that it will be 3D printed.  The interior of the box has four posts intended for attaching the PCB via the M3 mounting holes.

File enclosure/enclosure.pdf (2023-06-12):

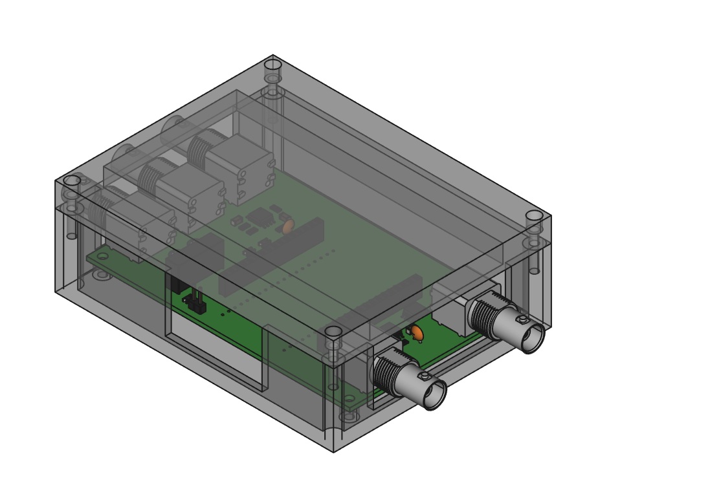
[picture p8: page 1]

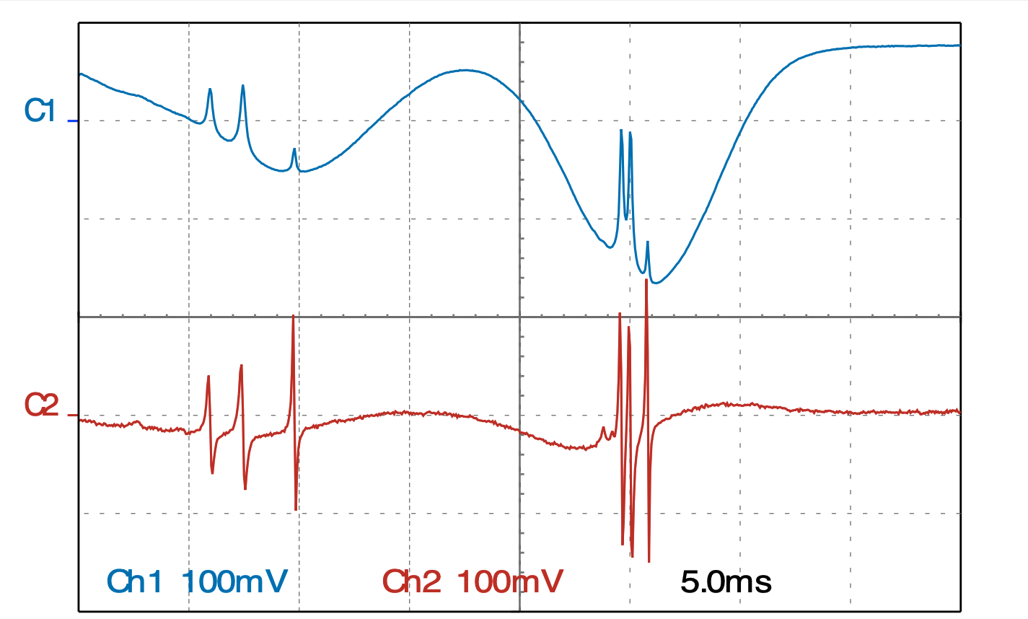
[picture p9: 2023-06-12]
assets/sas-spectrum-and-error.png

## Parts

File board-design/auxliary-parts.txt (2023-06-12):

"Digikey Part Number","Quantity","Description"
"S7017-ND","4","Female header for the ESP development board"
"2057-PH1-19-UA-ND","4","Male header for ESP development board"
"RMCF0603JT5K10CT-ND","10","0603, 5.1k resistor for DLC circuit board"

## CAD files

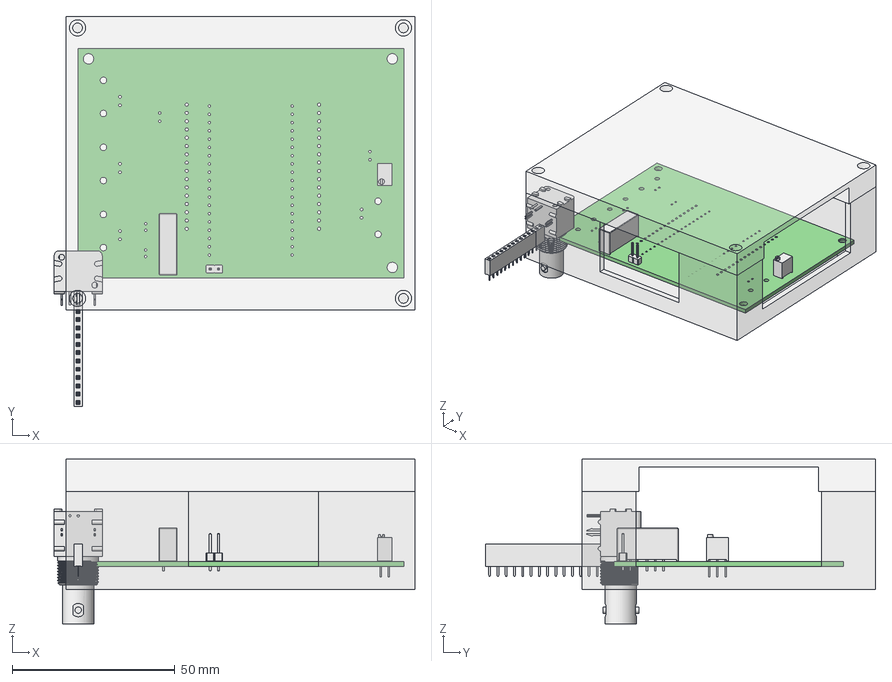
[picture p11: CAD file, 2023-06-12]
enclosure/moglabs-board-housing.FCStd
110.7 x 119.7 x 50.6 mm
Base
Top
D_1206_3216Metric
C_1206_3216Metric
R_1206_3216Metric
SOIC-8_5.275x5.275mm_P1.27mm
PinSocket_1x16_P2.54mm_Vertical
C_Disc_D5.0mm_W2.5mm_P2.50mm
PinHeader_1x02_P2.54mm_Vertical
Potentiometer_Bourns_3266W_Vertical
CP_Radial_D5.0mm_P2.00mm
Converter_DCDC_XP_POWER-IAxxxxS_THT
moglabs-remote-locking-board PCB

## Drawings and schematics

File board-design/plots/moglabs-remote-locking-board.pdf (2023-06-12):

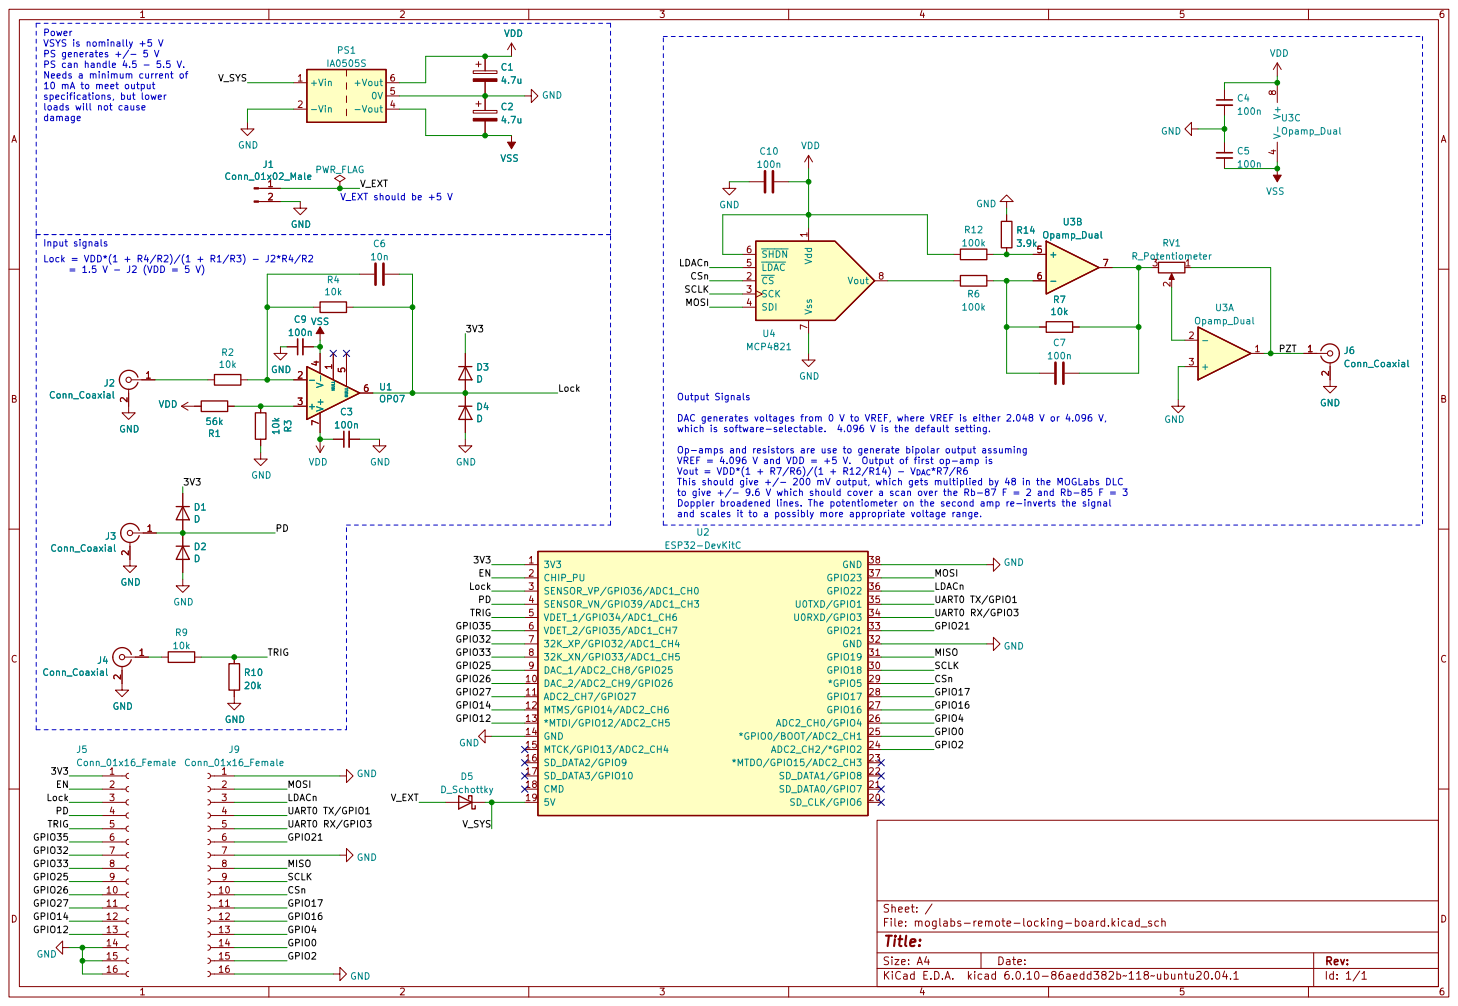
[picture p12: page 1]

Power VSYS is nominally +5 V

PS generates +/- 5 V
PS can handle 4.5 - 5.5 V. Needs a minimum current of 10 mA to meet output

specifications, but lower
loads will not cause
damage

10n GND GND
100n D5 D_Schottky R10
and scales it to a possibly more appropriate voltage range. V_EXT should be +5 V GND

1 ~{CS} 2 SCK 3 SDI 4 ~{LDAC} 5 ~{SHDN} 6 Vss 7 Vout 8 U4 MCP4821 GND GND

DAC generates voltages from 0 V to VREF, where VREF is either 2.048 V or 4.096 V,
which is software-selectable. 4.096 V is the default setting.

Op-amps and resistors are use to generate bipolar output assuming
VREF = 4.096 V and VDD = +5 V. Output of first op-amp is
Vout = VDD*(1 + R7/R6)/(1 + R12/R14) - V_{DAC}*R7/R6
This should give +/- 200 mV output, which gets multiplied by 48 in the MOGLabs DLC
to give +/- 9.6 V which should cover a scan over the Rb-87 F = 2 and Rb-85 F = 3
Doppler broadened lines. The potentiometer on the second amp re-inverts the signal

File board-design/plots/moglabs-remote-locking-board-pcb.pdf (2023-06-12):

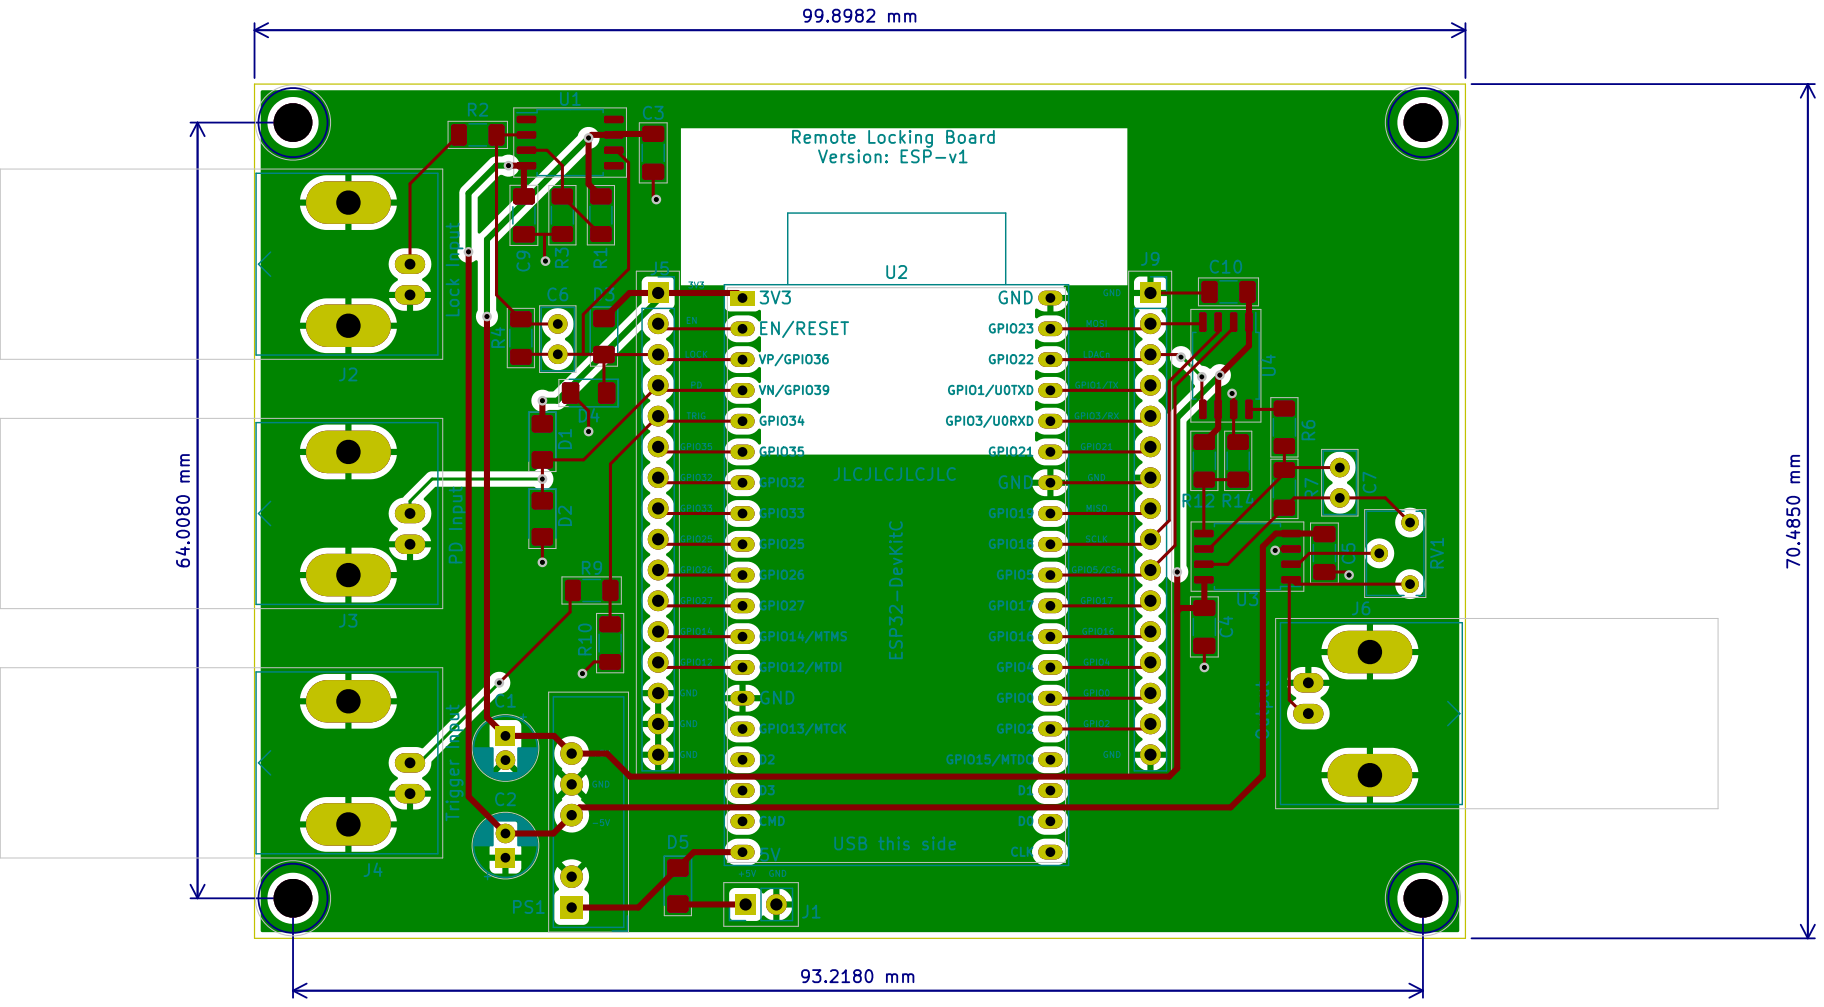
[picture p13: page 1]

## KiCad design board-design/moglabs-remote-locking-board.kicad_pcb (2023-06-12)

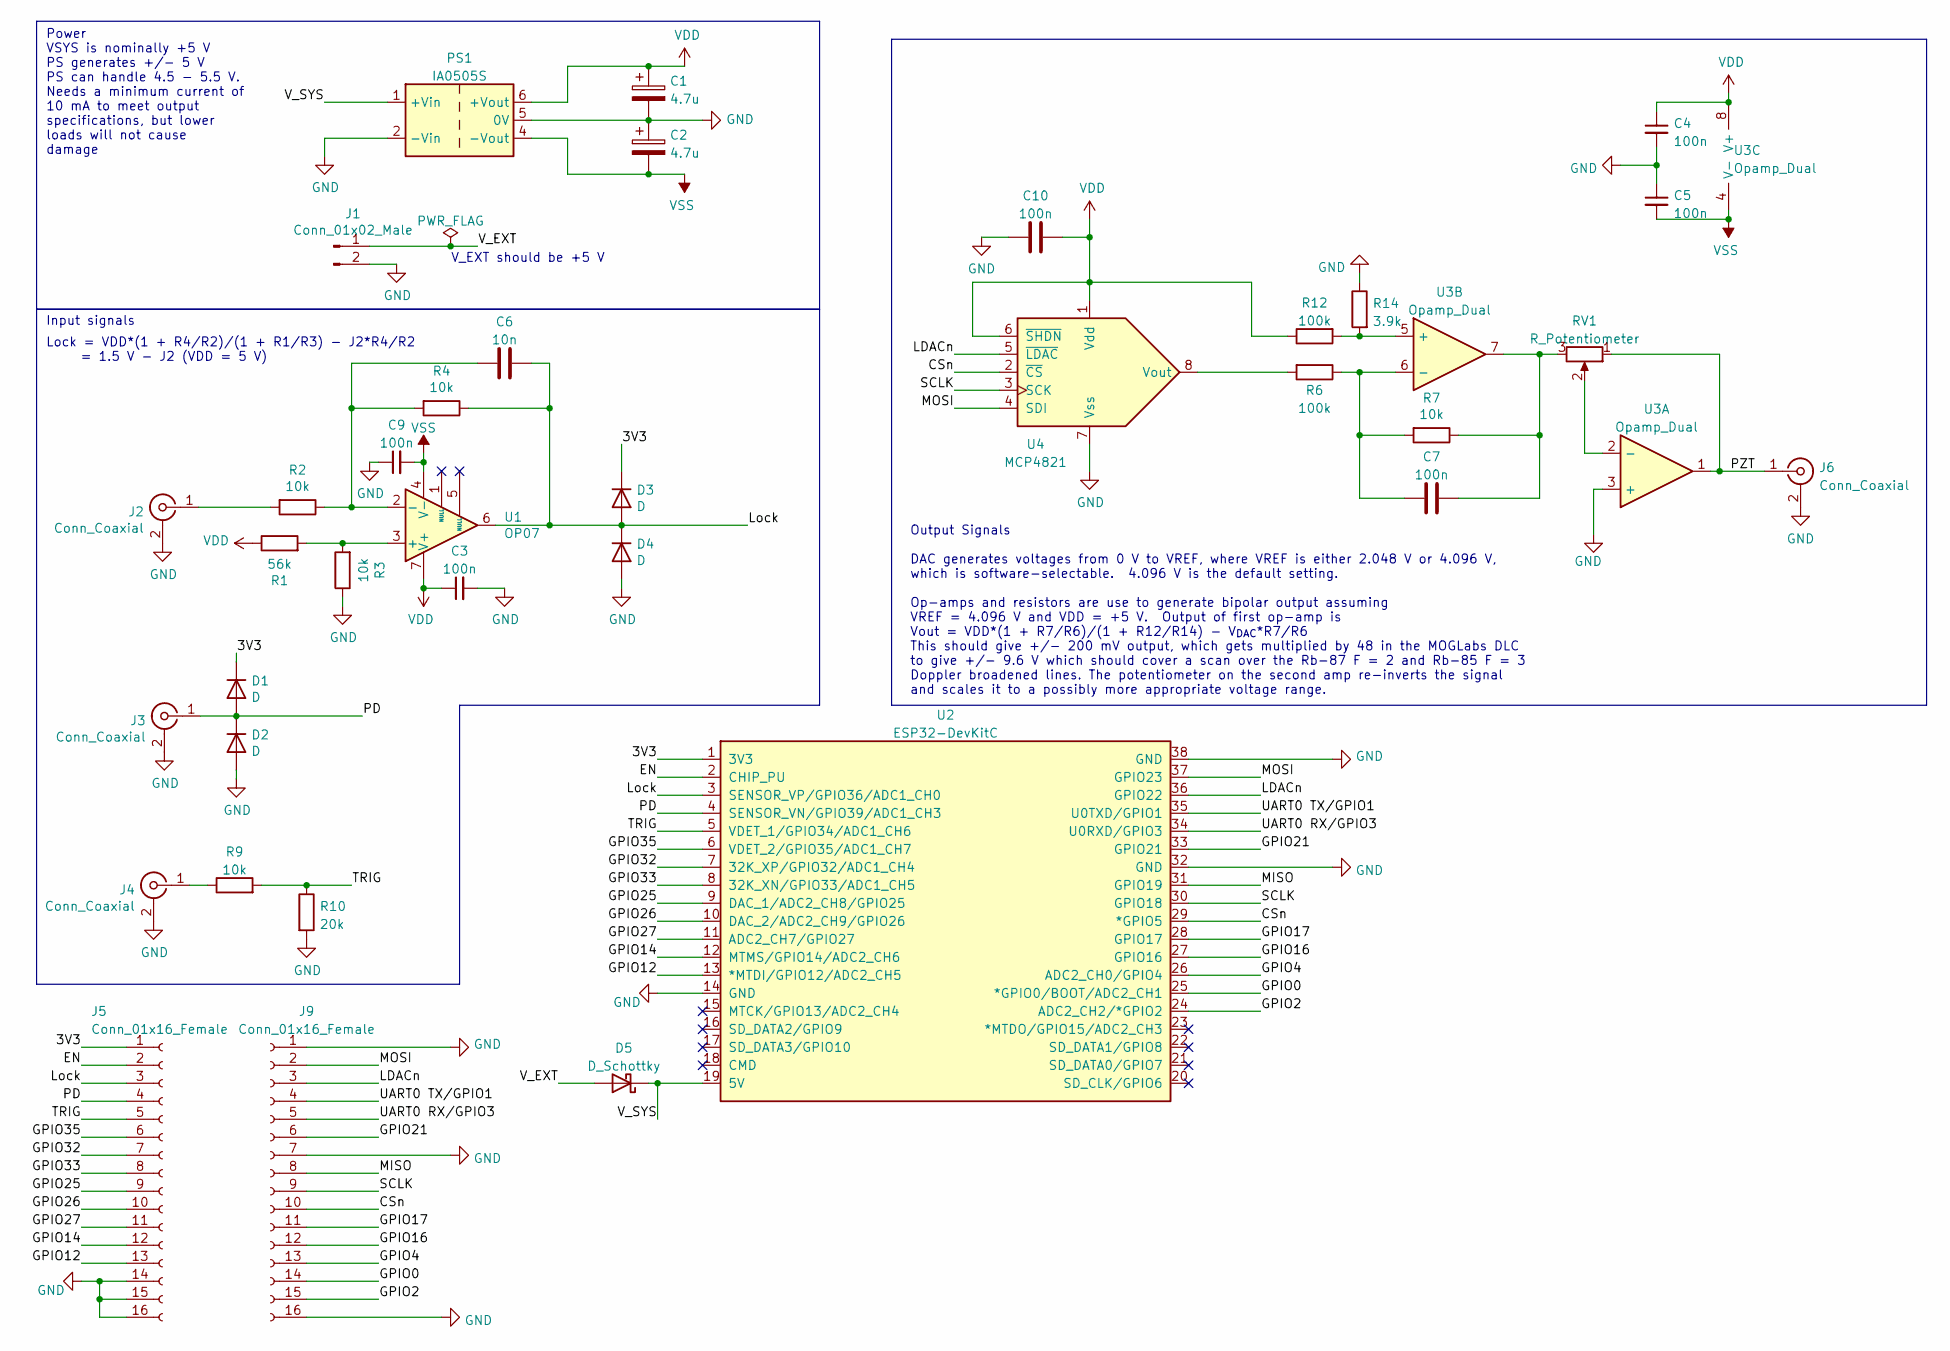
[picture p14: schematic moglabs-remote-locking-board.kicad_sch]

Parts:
C1, C2: 4.7u; CP_Radial_D5.0mm_P2.00mm; Digikey Part Number 732-8935-1-ND
C3, C4, C5, C9: 100n; C_1206_3216Metric_Pad1.33x1.80mm_HandSolder; Digikey Part Number 399-C1206C104K5RAC7210CT-ND
C6: 10n; C_Disc_D5.0mm_W2.5mm_P2.50mm
C7: 100n; C_Disc_D5.0mm_W2.5mm_P2.50mm
C10: 100n; C_1206_3216Metric_Pad1.33x1.80mm_HandSolder
D1, D2, D3, D4: D; D_1206_3216Metric_Pad1.42x1.75mm_HandSolder; Digikey Part Number 478-7809-1-ND
D5: D_Schottky; D_1206_3216Metric_Pad1.42x1.75mm_HandSolder; Digikey Part Number 478-7809-1-ND
J1: Conn_01x02_Male; PinHeader_1x02_P2.54mm_Vertical; Digikey Part Number 2057-PH1-02-UA-ND
J2, J3, J4, J6: Conn_Coaxial; BNC_Molex_0731000167; Digikey Part Number WM4089-ND
J5, J9: Conn_01x16_Female; PinSocket_1x16_P2.54mm_Vertical; Digikey Part Number 61301611821-ND
PS1: IA0505S; Converter_DCDC_XP_POWER-IAxxxxS_THT; Digikey Part Number 1470-IAB0105D05-ND
R1: 56k; R_1206_3216Metric_Pad1.30x1.75mm_HandSolder; Digikey Part Number RMCF1206JT56K0CT-ND
R2, R3, R4, R7, R9: 10k; R_1206_3216Metric_Pad1.30x1.75mm_HandSolder; Digikey Part Number RNCP1206FTD10K0CT-ND
R6, R12: 100k; R_1206_3216Metric_Pad1.30x1.75mm_HandSolder; Digikey Part Number 738-RNCP1206FTD100KCT-ND
R10: 20k; R_1206_3216Metric_Pad1.30x1.75mm_HandSolder; Digikey Part Number RNCP1206FTD20K0CT-ND
R14: 3.9k; R_1206_3216Metric_Pad1.30x1.75mm_HandSolder; Digikey Part Number RMCF1206FT3K90CT-ND
RV1: R_Potentiometer; Potentiometer_Bourns_3266W_Vertical; Digikey Part Number 987-1508-ND
U1: OP07; SOIC-8_5.23x5.23mm_P1.27mm; Digikey Part Number 296-TL081HIDRCT-ND
U2: ESP32-DevKitC; Digikey Part Number 1965-ESP32-DEVKITC-VE-ND
U3: Opamp_Dual; SOIC-8_5.23x5.23mm_P1.27mm; Digikey Part Number 296-LM2904BIDRCT-ND
U4: MCP4821; SOIC-8_5.275x5.275mm_P1.27mm; Digikey Part Number MCP4821T-E/SNCT-ND

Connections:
/3V3: D1.1 (K), D3.1 (K), J5.1, U2.1 (3V3)
/CSn: J9.10, U2.29 (*GPIO5), U4.2 (~CS)
/EN: J5.2, U2.2 (CHIP_PU)
/GPIO0: J9.14, U2.25 (*GPIO0/BOOT/ADC2_CH1)
/GPIO2: J9.15, U2.24 (ADC2_CH2/*GPIO2)
/GPIO4: J9.13, U2.26 (ADC2_CH0/GPIO4)
/GPIO12: J5.13, U2.13 (*MTDI/GPIO12/ADC2_CH5)
/GPIO14: J5.12, U2.12 (MTMS/GPIO14/ADC2_CH6)
/GPIO16: J9.12, U2.27 (GPIO16)
/GPIO17: J9.11, U2.28 (GPIO17)
/GPIO21: J9.6, U2.33 (GPIO21)
/GPIO25: J5.9, U2.9 (DAC_1/ADC2_CH8/GPIO25)
/GPIO26: J5.10, U2.10 (DAC_2/ADC2_CH9/GPIO26)
/GPIO27: J5.11, U2.11 (ADC2_CH7/GPIO27)
/GPIO32: J5.7, U2.7 (32K_XP/GPIO32/ADC1_CH4)
/GPIO33: J5.8, U2.8 (32K_XN/GPIO33/ADC1_CH5)
/GPIO35: J5.6, U2.6 (VDET_2/GPIO35/ADC1_CH7)
/LDACn: J9.3, U2.36 (GPIO22), U4.5 (~LDAC)
/Lock: C6.2, D3.2 (A), D4.1 (K), J5.3, R4.1, U1.6, U2.3 (SENSOR_VP/GPIO36/ADC1_CH0)
/MISO: J9.8, U2.31 (GPIO19)
/MOSI: J9.2, U2.37 (GPIO23), U4.4 (SDI)
/PD: D1.2 (A), D2.1 (K), J3.1 (In), J5.4, U2.4 (SENSOR_VN/GPIO39/ADC1_CH3)
/PZT: J6.1 (In), RV1.1, U3.1
/SCLK: J9.9, U2.30 (GPIO18), U4.3 (SCK)
/TRIG: J5.5, R9.2, R10.1, U2.5 (VDET_1/GPIO34/ADC1_CH6)
/UART0 RX/GPIO3: J9.5, U2.34 (U0RXD/GPIO3)
/UART0 TX/GPIO1: J9.4, U2.35 (U0TXD/GPIO1)
/V_EXT: D5.2 (A), J1.1
/V_SYS: D5.1 (K), PS1.1 (+Vin), U2.19 (5V)
GND: C1.2, C2.1, C3.2, C4.2, C5.1, C9.1, C10.2, D2.2 (A), D4.2 (A), J1.2, J2.2 (Ext), J3.2 (Ext), J4.2 (Ext), J5.14, J5.15, J5.16, J6.2 (Ext), J9.1, J9.7, J9.16, PS1.2 (-Vin), PS1.5 (0V), R3.1, R10.2, R14.1, U2.14 (GND), U2.32 (GND), U2.38 (GND), U3.3 (+), U4.7 (Vss)
unnamed: C6.1, R2.1, R4.2, U1.2 (-)
unnamed: J2.1 (In), R2.2
unnamed: J4.1 (In), R9.1
unnamed: R1.2, R3.2, U1.3 (+)
unnamed: C7.1, R6.1, R7.2, U3.6 (-)
unnamed: R6.2, U4.8 (Vout)
unnamed: R12.2, R14.2, U3.5 (+)
unnamed: RV1.2, U3.2 (-)
unnamed: C7.2, R7.1, RV1.3, U3.7
VDD: C1.1, C3.1, C4.1, C10.1, PS1.6 (+Vout), R1.1, R12.1, U1.7 (V+), U3.8 (V+), U4.1 (Vdd), U4.6 (~SHDN)
VSS: C2.2, C5.2, C9.2, PS1.4 (-Vout), U1.4 (V-), U3.4 (V-)

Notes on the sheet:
Power VSYS is nominally +5 V PS generates +/- 5 V PS can handle 4.5 - 5.5 V. Needs a minimum current of 10 mA to meet output specifications, but lower loads will not cause damage
V_EXT should be +5 V
Output Signals DAC generates voltages from 0 V to VREF, where VREF is either 2.048 V or 4.096 V, which is software-selectable. 4.096 V is the default setting. Op-amps and resistors are use to generate bipolar output assuming VREF = 4.096 V and VDD = +5 V. Output of first op-amp is Vout = VDD*(1 + R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
Input signals
Lock = VDD*(1 + R4/R2)/(1 + R1/R3) - J2*R4/R2 = 1.5 V - J2 (VDD = 5 V)

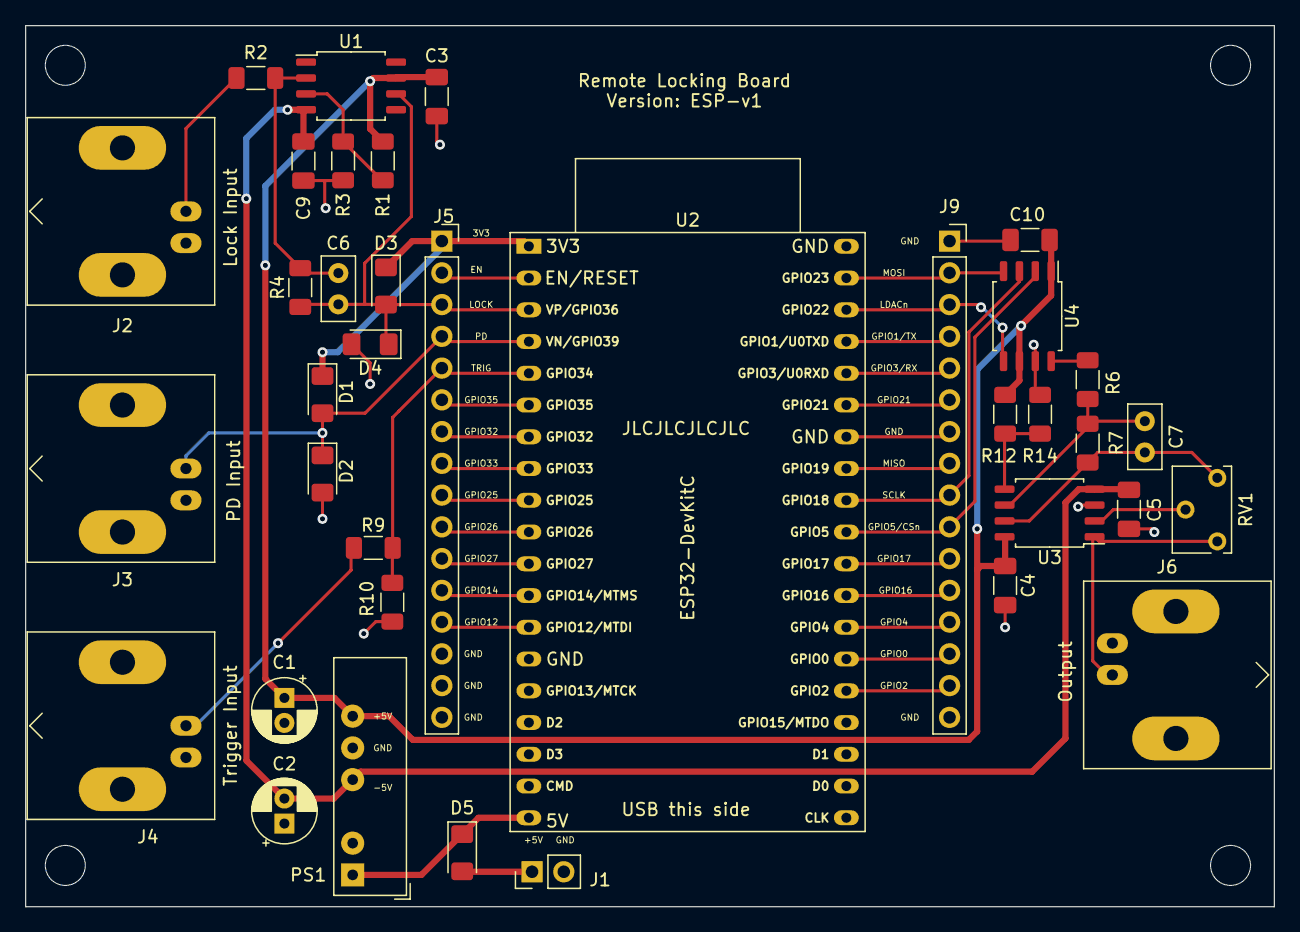
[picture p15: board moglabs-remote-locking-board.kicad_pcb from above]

Board: 2 copper layers, 99.9 x 70.5 mm, 37 parts (0 on the bottom side), 41 nets.

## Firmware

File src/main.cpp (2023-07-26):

/* ESP32 Remote Monitor and locking control for MOGLabs Diode Laser Controller

(c) Patrick Gleeson 2022

General notes:
- See TODO comments scattered throughout.
- HIGH and LOW are aliases for 1 and 0, respectively.
- TODO: track, report and client-command of LASER_ON and HOLD status.
*/

#include <Arduino.h>           // Framework
#include <ArduinoJSON.h>       // https://arduinojson.org/
#include <AsyncJson.h>         // For handling JSON packets
#include <ESPAsyncWebServer.h> // https://github.com/me-no-dev/ESPAsyncWebServer
#include <LittleFS.h>          // File-system
#include <SPI.h>
#include <WiFi.h>

#include <secrets.h> // in scr make a seacrets.h file and define the SSID and password MAke sure this is part of .gitignore


/* Pin mappings. With the Arduino framework, the pin number is the
ESP32 GPIO number (at least by default in PlatformIO)*/
#define PD_INPUT_PIN 39
#define LOCK_INPUT_PIN 36
#define TRIG_PIN 34

#define LED_PIN 2

#define SLOW_LOCK_PIN 14
#define FAST_LOCK_PIN 4
#define LASER_ON_PIN 21
#define HOLD_PIN 27

#define LDACN_PIN 22
#define VSPI_MOSI 23
#define VSPI_SCK 18
#define VSPI_CS 5
#define VSPI_MISO 19 // Not used
SPIClass *vspi = NULL; // Initialised in setup(). For DAC control.

/* Tracking the output state by reading the appropriate output pin
values is unreliable, so record it explicitly: */
bool slow_lock = false;
bool fast_lock = false;
bool hold = false;
bool laser_on = false;

/* Settings and storage for data sampling. Resolution and duration are specified externally (client, config file) in milliseconds, but are handled
internally in microseconds.*/
#define MIN_RES 100               // microseconds. int.
#define MIN_DURATION 30000.0      // Else ESP32 can become unresponsive. Float.
#define MAX_DURATION 20000000.0   // 20 sec. (float)
#define CHANNEL_BUFFER_SIZE 16384 // 16KB per channel, enough for 10s data at 1ms resolution.
/* A new packet will be started if the buffer gets full, regardless of sampling
settings*/
uint8_t input_buffer[2 * CHANNEL_BUFFER_SIZE]; // Alternating PD & error samples.

unsigned int time_resolution = 2000;  // Microseconds
unsigned int next_resolution = 2000;  // For next packet.
unsigned int sample_duration = 40000; // Microseconds

uint64_t packet_start;  // Packet start time (microseconds);
uint64_t elapsed = 0;   // Since start of packet (microseconds)
unsigned int N = 0;     // Datapoint index in current packet
uint64_t trig_time = 0; // Most recent trigger time (microseconds)

// Create AsyncWebServer object on port 80
AsyncWebServer server(80);
AsyncWebSocket ws("/ws");

// Send value to external MCP4821 DAC.
// Similar to https://cyberblogspot.com/how-to-use-mcp4921-dac-with-arduino/
// but the bytes sent have been adjusted so it works.
void set12BitDAC(uint16_t value) {
  Serial.println(value);
  uint16_t data = 0b0001000000000000 | value; // could go directly to secondByte
  // 4 config bits + most significant 4 value bits
  uint8_t firstByte = 0b00010000 | ((uint8_t)((value & 0xFFF) >> 8));
  // remaining 8 value bits
  uint8_t secondByte = (uint8_t) data;
  //Serial.println(firstByte, BIN);
  //Serial.println(secondByte, BIN);
  digitalWrite(vspi->pinSS(), LOW); // VSPI_CS; pull low to prep other end for transfer
  /* Use SPI clock rate 16MHz (MCP4821 supports up to 20MHz). We use SPI_MODE0,
  where the clock is LOW when idle and data is transferred on the rising edge.*/
  vspi->beginTransaction(SPISettings(16000000, MSBFIRST, SPI_MODE0));
  vspi->transfer(firstByte);
  vspi->transfer(secondByte);
  vspi->endTransaction();
  // pull ss (CS) high to signify end of data transfer
  digitalWrite(vspi->pinSS(), HIGH); 
  /* Data value will be immediately translated to VOUT, as LDACn is set
   permanently LOW in setup().*/
}

/* Handle an incoming WebSocket message. These are expected to be 12-bit
level values for the external MCP4821 DAC. */
void handleWebSocketMessage(void *arg, uint8_t *data, size_t len) {
  AwsFrameInfo *info = (AwsFrameInfo *)arg;
  if (info->final && info->index == 0 && info->len == len && info->opcode == WS_BINARY) {
    /* Received a single binary packet. This is expected to contain two bytes,
    forming a 16 bit integer (most-significant byte first). The 12
    least-significant bits are our DAC value. */
    set12BitDAC((((uint16_t)data[0]) << 8) | ((uint16_t)data[1]));
    // Obsolete: dacWrite(pin, 8-bit value) for ESP32's inbuilt 8-bit DAC.
  }
}

// Handler for WebSocket events
void onWsEvent(AsyncWebSocket *server, AsyncWebSocketClient *client, AwsEventType type, void *arg, uint8_t *data, size_t len) {
  switch (type) {
  case WS_EVT_CONNECT:
    Serial.printf("WebSocket client #%u connected from %s\n", client->id(), client->remoteIP().toString().c_str());
    break;
  case WS_EVT_DISCONNECT:
    // Could initiate sleep here.
    Serial.printf("WebSocket client #%u disconnected\n", client->id());
    break;
  case WS_EVT_DATA:
    handleWebSocketMessage(arg, data, len);
    break;
  case WS_EVT_PONG:
  case WS_EVT_ERROR:
    break;
    // I'm fairly sure this exhausts all possible event types.
  }
}

// Update
void setSampleSettings(double resolution, double duration) {
  /* Arguments are in milliseconds and converted to microseconds for
  next_resolution and sample_duration. Duration takes effect immediately but
  resolution waits until a new packet, so that samples remain evenly spaced. */
  next_resolution = max((int)(resolution * 1000), MIN_RES); // Hard limit 0.1ms res
  sample_duration = (int)min(max(
                                 max(duration * 1000, 2.0 * next_resolution), MIN_DURATION),
                             MAX_DURATION);
  /* Hard duration min 30ms and max 20sec, else ESP can become unresponsive.
  Also enforce duration > 2*resolution, to ensure >1 samples. */
  Serial.println(" Sampling settings set to:");
  Serial.printf("  Resolution: %.1f ms\n", next_resolution / 1000.0);
  Serial.printf("  Duration: %.1f ms\n", sample_duration / 1000.0);
  Serial.println();
}

// Handle a HTTP request to update sampling settings
void settingsHandler(AsyncWebServerRequest *request, JsonVariant &json) {
  const JsonObject &jsonObj = json.as<JsonObject>();
  setSampleSettings(jsonObj["resolution"], jsonObj["duration"]);
  request->redirect("/get_sample_settings");
}

/* Record the time of a trigger interrupt. Interrupts need to be in IRAM for
fast access (hence IRAM_ATTR). */
void IRAM_ATTR onTrig() {
  trig_time = micros();
}


//#################################SETUP#############################################//

// Setup code, is run once upon restart.
void setup() {
  // dac.begin(VSPI_CS);
  //  Serial port for debugging purposes
  Serial.begin(115200); // 115200 is baud rate (symbol communication rate)

  // Output pins
  pinMode(LED_PIN, OUTPUT); // ESP32 devkit onboard LED
  pinMode(SLOW_LOCK_PIN, OUTPUT);
  pinMode(FAST_LOCK_PIN, OUTPUT);
  pinMode(LASER_ON_PIN, OUTPUT);
  pinMode(HOLD_PIN, OUTPUT);
  pinMode(LDACN_PIN, OUTPUT);

  vspi = new SPIClass(VSPI);
  vspi->begin(VSPI_SCK, VSPI_MISO, VSPI_MOSI, VSPI_CS); // SCK, MISO, MOSI, SS
  pinMode(vspi->pinSS(), OUTPUT);

  /* SPI API info: https://docs.espressif.com/projects/arduino-esp32/en/latest/api/spi.html and links therein */

  // Initial output values
  digitalWrite(SLOW_LOCK_PIN, LOW);
  digitalWrite(FAST_LOCK_PIN, LOW);
  digitalWrite(LASER_ON_PIN, LOW);
  digitalWrite(HOLD_PIN, LOW);
  digitalWrite(LDACN_PIN, LOW); // So DAC input is automatically applied.
  // LDACN control is a likely 
  // Laser will not turn on if SLOW is HIGH.

  digitalWrite(LED_PIN, LOW); // Indicate that board is running.
  // LED pin is inverted: LOW is on.

  // Input pins
  pinMode(PD_INPUT_PIN, INPUT);   // Photodiode channel.
  pinMode(LOCK_INPUT_PIN, INPUT); // Error signal.
  pinMode(TRIG_PIN, INPUT);
  attachInterrupt(TRIG_PIN, onTrig, RISING); // Record any triggers

  // Begin filesystem
  if (!LittleFS.begin()) {
    Serial.println("An error has occurred while mounting LittleFS.");
  }

  // Load config from JSON file.
  File configFile = LittleFS.open("/config.json", "r");
  if (!configFile) {
    Serial.println("Unable to access configuration file.");
  }

  StaticJsonDocument<512> configDoc;
  DeserializationError error = deserializeJson(configDoc, configFile);
  if (error) {
    Serial.println("Invalid configuration file.");
  }

  static char name[100];
  strcpy(name, configDoc["name"]); // Laser display name (Defaults to NULL)

  // Default sampling settings
  const double configRes = configDoc["default_resolution"];
  const double configDur = configDoc["default_duration"];
  setSampleSettings(
      configRes ? configRes : 2.0,
      configDur ? configDur : 60.0);

  // WiFi details
  const bool host = configDoc["host"]; /* Whether to host own network (mainly
  for testing). If not found in the config file, this value will default to
  false (zero). */

  // Network defaults
  IPAddress local_ip(192, 168, 1, 1); // How we appear to other devices on the network
  IPAddress gateway(192, 168, 1, 1);  /* local device through which connections
  external to the local network are routed (i.e. in this case, the board).
  These connections will fail, because the board isn't connected to the
  internet.*/
  IPAddress subnet(255, 255, 255, 0); // Allows extraction of network address from local address

  const char *ip_str = configDoc["default_ip"];
  if (ip_str) {
    local_ip.fromString(ip_str);
    gateway.fromString(ip_str);
  }

  /* Connect to Wi-Fi. Modes:
  - Station (STA): connects to existing WiFi.
  - Access Point (AP): hosts its own network. By default limited to 4
    connected devices; this can be increased up to 8. Below, we limit it to 1.
  */

  WiFi.disconnect();
  // WiFi.setAutoConnect(false);

  if (host) { // Set up own network
    // wifi_set_phy_mode(PHY_MODE_11G);
    //get these from the secrets.h file
    const char *host_ssid = configDoc["host_ssid"];
    const char *host_password = configDoc["host_password"];
    if (!(host_ssid && host_password)) {
      Serial.println("Missing host_ssid or host_password.");
    }
    if (strlen(host_password) < 8) {
      Serial.println("Warning: WiFi.softAP (hosting) will fail if host_password has fewer than 8 characters.");
    }
    int host_channel = configDoc["host_channel"]; // Specifies the WiFi frequency band. 1-11 is fairly safe in most countries. Default is 1.
    if (!host_channel) {
      host_channel = 1;
    }
    const int max_connection = 1;
    /* Prevents multiple clients. From the documentation: "Once the max number
    has been reached, any other station that wants to connect will be forced
    to wait until an already connected station disconnects."*/
    WiFi.mode(WIFI_AP);
    Serial.print("Setting soft-AP configuration ... ");
    Serial.println(WiFi.softAPConfig(local_ip, gateway, subnet) ? "Ready" : "Failed!");
    Serial.print("Setting soft-AP ... ");
    Serial.println(WiFi.softAP(host_ssid, host_password, host_channel, false, max_connection) ? "Ready" : "Failed!");
    // Pretty sure this uses WPA2 security protocol (i.e. the most common).
    Serial.print("Soft-AP IP address = ");
    Serial.println(WiFi.softAPIP());
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

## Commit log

2023-01-03 Initial commit, board designed with Raspberry Pi Pico W.
    [moglabs-remote-locking-board.kicad_pcb, moglabs-remote-locking-board.kicad_sch, moglabs-remote-locking-board.sch]
2023-01-04 Made FreeCAD model of housing w/o BNC holes
    [moglabs-board-housing.FCStd, moglabs-remote-locking-board.kicad_pcb]
2023-01-19 Minor changes to enclosure
    [moglabs-board-housing.FCStd]
2023-01-24 Updated path for footprints. Generated PDF of schematic
    [moglabs-remote-locking-board.kicad_pcb]
2023-01-25 Changed microcontroller to ESP12-DEVKIT-C. Updated FreeCAD design
    [moglabs-board-housing.FCStd, moglabs-remote-locking-board.kicad_pcb, moglabs-remote-locking-board.kicad_sch]
2023-01-25 Updated input/output connectors to headers, modified board and FreeCAD
    [moglabs-board-housing.FCStd, moglabs-remote-locking-board.kicad_pcb, moglabs-remote-locking-board.kicad_sch]
2023-01-26 Finialized design with pin headers for outputs. Added README
    [moglabs-board-housing.FCStd, moglabs-remote-locking-board.kicad_pcb]
2023-01-26 Inputs/outputs now connected via BNC right-angle connectors.
    FreeCAD enclosure modified to account for new connectors. Board
    size is larger than previous version.
    [moglabs-board-housing.FCStd, moglabs-remote-locking-board.kicad_pcb, moglabs-remote-locking-board.kicad_sch]
2023-01-30 Added voltage divider on trig input, changed output voltage range
    Also made board smaller for cheaper manufacturing.
    [moglabs-board-housing.FCStd, moglabs-remote-locking-board.kicad_pcb, moglabs-remote-locking-board.kicad_sch]
2023-01-30 Removed current output, changed DAC to single channel
    Current input on the MOGLabs DLC doesn't allow for a DC bias in
    the absence of the fast lock. So I removed the current output,
    and therefore removed the 2 channel DAC. I have kept the 2 channel
    op-amp, and now I have two inverting amplifiers where the gain of the
    second stage can be adjusted through a trimpot.
    [moglabs-board-housing.FCStd, moglabs-remote-locking-board.kicad_pcb, moglabs-remote-locking-board.kicad_sch]
2023-06-12 Move enclosure to subdirectory
    [moglabs-board-housing.FCStd]
